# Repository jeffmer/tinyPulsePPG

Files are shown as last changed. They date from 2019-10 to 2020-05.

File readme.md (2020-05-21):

# tinyPulsePPG

This project implemented on an ATTiny85 displays a moving Photoplethysmogram together with pulse rate and estimates of SpO2 - blood oxygen percentage. It uses an SSD1306 128x32 OLED display and a Max30102 sensor. It is emphasised that this should **not be used for medical purposes**. The computation of SpO2 is very approximate and not calibrated in any way. The project is an exercise in software and hardware parsimony.

### Hardware
The system was implemented on a prototyping board as shown below:

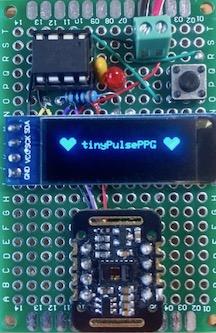
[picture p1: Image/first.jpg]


The circuit diagram is:

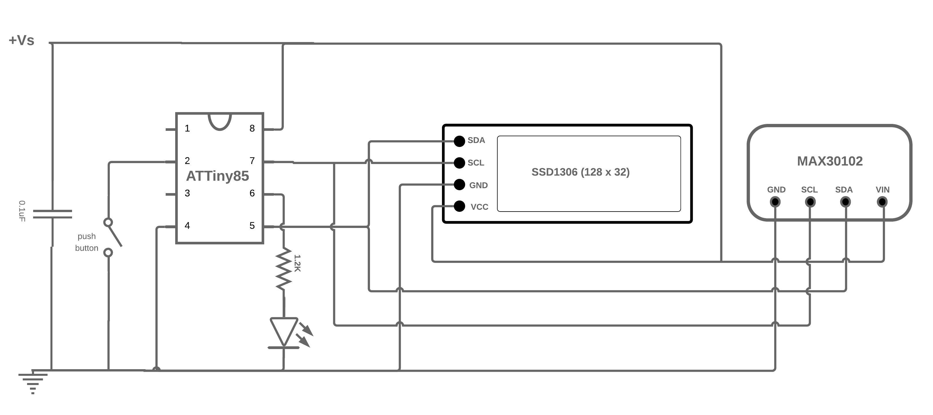
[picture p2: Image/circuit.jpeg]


The ATTiny85 is configured to run at 16 MHz using Spence Konde's ATTinyCore. Consequently, according to the datasheet, the supply voltage should be >4.5V. In fact, it seems to run quite happily from a lipo battery (3.7 - 4.2V).

### Operation

After a few seconds the following screen is displayed:

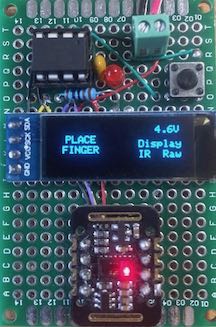
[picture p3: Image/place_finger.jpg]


When a finger is placed on the sensor, the PPG, heart-rate and two estimates of blood oxygen are displayed (discussed below):

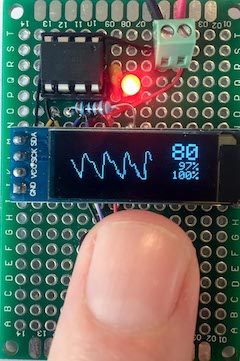
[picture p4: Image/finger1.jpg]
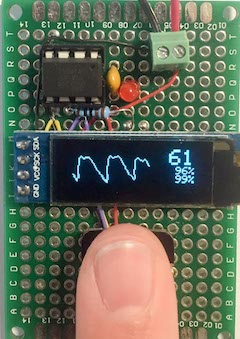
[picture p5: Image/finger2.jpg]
 ..........  

The red led pulses once per heart beat. The PPG display is updated every 50ms.

### Software

**Needed library**
In order to build this to the ATTiny85 you need to install the library ATTinyCore
This core can be installed using the boards manager. The boards manager URL is:

http://drazzy.com/package_drazzy.com_index.json

File->Preferences on a PC, or Arduino->Preferences on a Mac, enter the above URL in "Additional Boards Manager URLs
Tools -> Boards -> Boards Manager... *If using 1.6.6, close boards manager and re-open it (see below)
Select "ATTinyCore by Spence Konde" and click "Install".

**Driver issue -** The Maxim max30102 sensor used is mounted on a MH-ET LIVE breakout board. The Maxim datasheet for the max30102 implies but does not state explicitly that LED1 is Red and LED2 is Infrared (IR), however, if the amplitude of LED1 is set to zero, the red led (as depicted in the *place finger*) picture remains lit, while if LED2 is set to zero, the red led is extinguished. The obvious conclusion is that LED1 is IR and LED2 is Red (i.e. swapped) which also works when computing blood oxygen - see below. I mention this as the most common driver used in Arduino projects for the max30102 is the Sparkfun 3010x driver which clearly identifies LED1 with Red and LED2 with IR. This may be true for the max30105 device mounted on the Sparkfun board but does not seem to apply to the max30102 on the MH-ET-LIVE board. 

**Spo2 calculation** *"SpO2 stands for peripheral capillary oxygen saturation, an estimate of the amount of oxygen in the blood. More specifically, it is the percentage of oxygenated haemoglobin (haemoglobin containing oxygen) compared to the total amount of haemoglobin in the blood (oxygenated and non-oxygenated haemoglobin)."* 

Oxygenated haemoglobin and deoxygenated haemoglobin have different light absorption characteristics for red and IR wavelengths. This is the basis for sensors like the max30102. The calculation uses the ratio:

`R = (AC_red/DC_red)/(AC_IR/DC_IR)`

where `AC_xxx `is the fluctuating component of the xxx signal and `DC_xxx` is the fixed component. **tinyPulsePPG** uses R in two different formulas. The upper percentage is from the classic formula:

`R = 104 - 1.7 * R`

The lower uses a table from the Maxim Arduino driver which is an approximation of the formula:

`-45.060 * R * R + 30.354 * R + 94.845`

The AC is computed in **tinyPulsePPG** as the peak to peak amplitude of the signal after the DC element has been removed.  the DC element is computed by an exponential moving average filter and the AC is also filtered. I have not experimented enough with the constants in these filters to determine the effect on the SpO2 calculation or indeed how reliable this method is of computing these quantities.

**PPG display** The read and IR signals from the sensor go through two stages of filtering. The first as described above is removal of the DC element. The second is a moving average filter which acts as a low pass filter to remove transients before the signal is input to the beat detector. I have chosen to display the signal after the first filtering phase so that it retains more interesting features. 

For example, dicrotic notches can be seen in the pictures above - *"a secondary upstroke in the descending part of a pulse tracing corresponding to the transient increase in aortic pressure upon closure of the aortic valve. - Merriam Webster Dictionary"*

I have noticed that if this dicrotic notch is particularly strong - younger individuals - it can overcome the second stage filtering and cause erroneous output from the beat detector which essentially looks for peaks and valleys in the wave. On going work!

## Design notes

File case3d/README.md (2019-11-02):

# tinyPulsePPG - 3d printed case

The directory contains the STL files for the top and bottom of the case and the OpenScad used to generate them. 
You will need to adjust the Height of the case and the BoardHeight to fit your board and battery. The board pictured below is lower profile than the original versio (8mm).

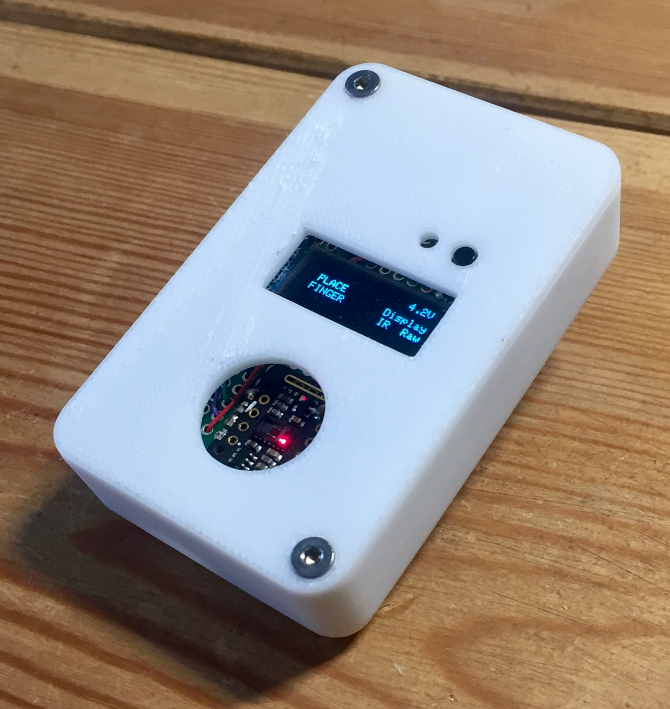
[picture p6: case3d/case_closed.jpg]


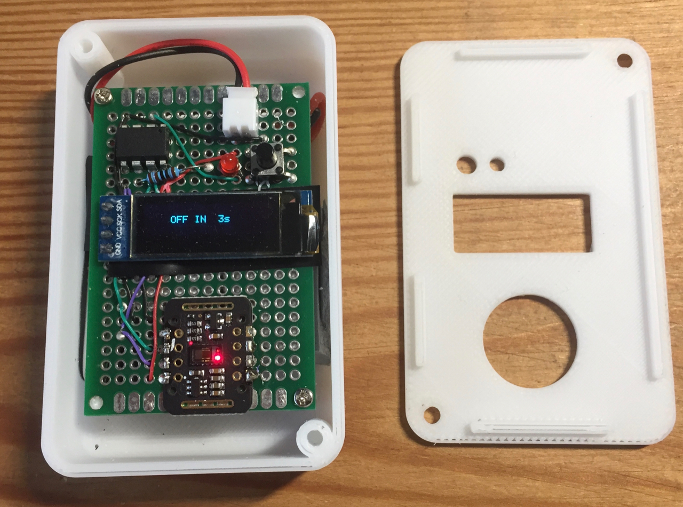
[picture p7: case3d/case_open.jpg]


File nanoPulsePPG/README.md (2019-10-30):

# arduinoPulsePPG

A version of tinyPulsePPG that runs on an Arduino AVR platform - tested on a Nano.

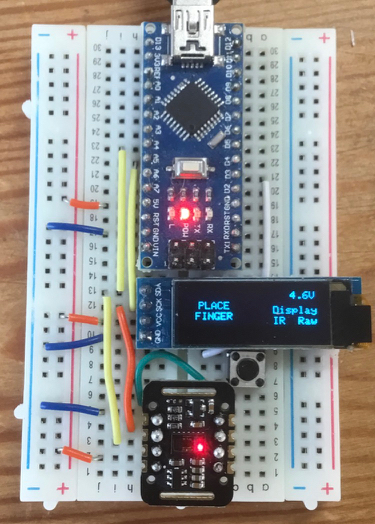
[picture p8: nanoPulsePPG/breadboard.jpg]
breadboard


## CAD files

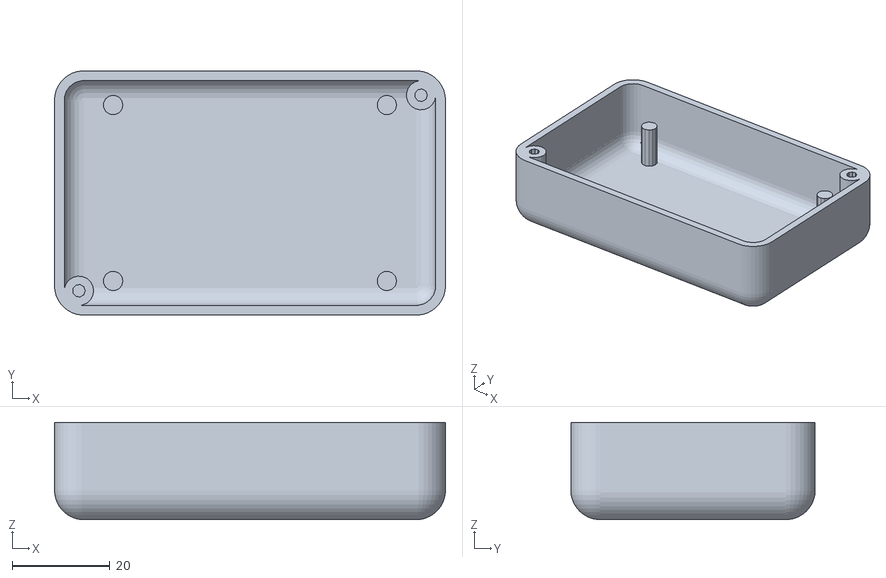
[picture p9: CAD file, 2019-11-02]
case3d/tinyPulsePPG_bottom.stl
80.0 x 50.0 x 19.9

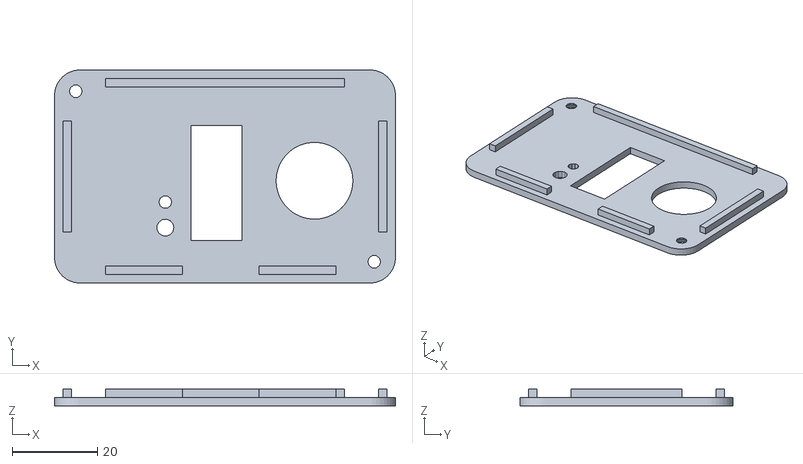
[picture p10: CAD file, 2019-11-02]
case3d/tinyPulsePPG-top.stl
80.0 x 50.0 x 3.90

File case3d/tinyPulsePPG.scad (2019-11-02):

$fa = 1.0;
$fs = 1.0;
Length = 80;
Width  = 50;
Height = 20;
Thick = 2;
Rnd    = 6;
BoardHeight = 8;

use <MCAD/boxes.scad>

module pillar(h,r) {
    difference() {
        union() {
            color("blue") cylinder(h=h,r=r);
            color("red")sphere(r=r);
        }
        translate([0,0,h/2]) cylinder(h=(h/2+1),r=1.3);
    }
}

module bottomBox(size,r){
    difference(){
        translate([size[0]/2, size[1]/2,(size[2]+r)/2]) 
            roundedBox([size[0],size[1],size[2]+r],r,false);
        translate([0,0,size[2]-0.1])
            cube([size[0],size[1],r+1]);
    }
}

module bottomCase(size,r,thick,bh){
    difference(){
        bottomBox(size,r);
        translate([thick,thick,thick]) 
            bottomBox([size[0]-thick*2, size[1]-thick*2, size[2]],r-thick);
    }
    translate([size[0]-r+1,size[1]-r+1,r-1])
        pillar(h=size[2]-r+0.88,r=3);
    translate([r-1,r-1,r-1])
        pillar(h=size[2]-r+0.88,r=3);
    translate([12,7,0.2])
        color("red") cylinder(h=size[2]-bh,r=2);
    translate([12,43,0.5])
        color("red") cylinder(h=size[2]-bh,r=2);
    translate([68,7,0.5])
        color("red") cylinder(h=size[2]-bh,r=2);
    translate([68,43,0.5])
        color("red") cylinder(h=size[2]-bh,r=2);
 }

bottomCase([Length,Width,Height],Rnd,Thick,BoardHeight);

module screwhole(thick) {
    color("red") {
        translate([0,0,-0.2]) cylinder(h=1.8,r1=3.0,r2=1.5);
        cylinder(h=thick*2,r=1.5);
    }
}

    
module topPlate(len,wid,r,thick){
    difference(){
        union() {
            translate([len/2,wid/2,thick/2])
                roundedBox([len,wid,thick],r,true);
        }
        translate([32,10,-thick])
            cube([12, 27, thick*3]);
       translate([26,13,-0.2])
            cylinder(h=thick*2,r=2); 
        translate([26,19,-0.2])
            cylinder(h=thick*2,r=1.5); 
        translate([61,24,-0.2])
            cylinder(h=thick*2,r=9); 
        translate([r-1,wid-r+1,0])
             screwhole(thick);
        translate([len-r+1,r-1,0])
             screwhole(thick);
    }
   translate([thick,2*r,thick-0.1])
       color("red") cube([thick,wid-4*r,thick]);
   translate([len-2*thick,2*r,thick-0.1])
       color("red") cube([thick,wid-4*r,thick]);
   translate([2*r,thick,thick-0.1])
       color("green") cube([30-2*r,thick,thick]);
   translate([2*r+36,thick,thick-0.1])
       color("green") cube([30-2*r,thick,thick]);
   translate([2*r,wid-2*thick,thick-0.1])
       color("green") cube([len-4*r,thick,thick]);


}

//topPlate(Length,Width,Rnd,Thick);

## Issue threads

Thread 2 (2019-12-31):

### ISSUE TITLE
Adding BME280 sensor Data

### ISSUE THREAD

**Issue by OhioJoe** [jeffmer/tinyPulsePPG#2]
I am using a 128x64 ssd1306. I can write data to oled display's lower half. I would like to have the PulseOxy data display on the first 31 lines and the BME sensor data display on lines 33-63. 
I can add 'test' data ie: temp = 98.6 but cannot figure out how to add live data.
I added a function to calculate the variables, but calling the function hangs the program.  

> void draw_oled(int msg) {
>   oled.firstPage();
> 
>   do {
>     switch (msg) {
>       case 0:  oled.drawStr(10, 0, F("Device error"), 1);
>         break;
>       case 1:
>         oled.drawStr(13, 2, F("PLACE"), 1); //13,10
>         oled.drawStr(10, 16, F("FINGER"), 1); //10,20
>         oled.drawChar(100, 0, voltage / 10 + '0');
>         oled.drawChar(106, 0, '.');
>         oled.drawChar(112, 0, voltage % 10 + '0');
>         oled.drawChar(118, 0, 'V');
>         oled.drawStr(84, 16, F("Display"), 1); //84,14
>         oled.drawStr(0, 34, F("T: "), 1);
>         oled.drawChar(26, 34,  'F');
> //        temp = 1.8 * bme280.readTemperature() + 32;
>         temp = 98.6;
>         //        Serial.println(temp);
>         print_digit(12, 34, temp, "F", 2, 1);
>         oled.drawStr(64, 34, F("H: "), 1);
>         print_digit(76, 34, humi, "F", 2, 1);
>         oled.drawChar(94, 34,  '%');
>         oled.drawStr(0, 45, F("Alt: "), 1);
> 
>         print_digit(25, 45, alt, "F", 3, 1);
>         oled.drawStr(0, 57, F("P: "), 1);
>         print_digit(12, 57, pres, "F", 3, 1);
>         oled.drawStr(34, 57, F("mmHg"), 1);
>         if (draw_Red)
>           oled.drawStr(84, 24, F("Red"), 1);
>         else
>           oled.drawStr(84, 24, F("IR"), 1);
>         if (filter_for_graph)
>           oled.drawStr(108, 24, F("Avg"), 1);
>         else
>           oled.drawStr(108, 24, F("Raw"), 1);
>         break;

**Comment by jeffmer** [comment]
I would suggest you make temp a global variable and call your function in the main program loop. The problem is that to avoid having a large buffer the draw routines are called multiple times. I suspect you are hanging due to an i2c conflict.

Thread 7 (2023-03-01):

### ISSUE TITLE
Image example usage

### ISSUE THREAD

**Issue by Arritmic** [jeffmer/tinyPulsePPG#7]
Hi @jeffmer ,

Could I use one of the images of the device prototype in my thesis?
If yes, how should I reference you??

Best,
Arritmic

**Comment by jeffmer** [comment]
Yes of course, feel free to use it. Simply reference the github repository would be fine. 

BTW: what is your thesis about?

**Comment by Arritmic** [comment]
It is about remote photoplethysmography and remote ballistography using cameras and radars. It includes from development of novel algorithms, to use cases and implementation in embedded devices.

**Comment by jeffmer** [comment]
That sounds like a lot of fun. I am a retired computing science academic - would love to see your thesis when you finish it - I am sure you will put a PDF on line.

**Comment by Arritmic** [comment]
Yes, sure!! It will be an honor. Please, find my humble contribution in google scholar: https://scholar.google.fi/citations?user=vLYIwqUAAAAJ&hl=en

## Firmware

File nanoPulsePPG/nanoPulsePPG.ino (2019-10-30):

/*
*  ATTiny84 - Pulse Oximeter with PPG display
*  DEFINITELY NOT FOR MEDICAL USE
*
* j.n.magee 15-10-2019
*/

#include "ssd1306h.h"
#include "MAX30102.h"
#include "Pulse.h"
#include <avr/pgmspace.h>
#include <EEPROM.h>
#include <avr/sleep.h>

// Routines to clear and set bits 
#ifndef cbi
#define cbi(sfr, bit) (_SFR_BYTE(sfr) &= ~_BV(bit))
#endif
#ifndef sbi
#define sbi(sfr, bit) (_SFR_BYTE(sfr) |= _BV(bit))
#endif


SSD1306 oled; 
MAX30102 sensor;
Pulse pulseIR;
Pulse pulseRed;
MAFilter bpm;

#define LED LED_BUILTIN
#define BUTTON 3
#define OPTIONS 7

static const uint8_t heart_bits[] PROGMEM = { 0x00, 0x00, 0x38, 0x38, 0x7c, 0x7c, 0xfe, 0xfe, 0xfe, 0xff, 
                                        0xfe, 0xff, 0xfc, 0x7f, 0xf8, 0x3f, 0xf0, 0x1f, 0xe0, 0x0f,
                                        0xc0, 0x07, 0x80, 0x03, 0x00, 0x01, 0x00, 0x00, 0x00, 0x00, 
                                        0x00, 0x00 };

//spo2_table is approximated as  -45.060*ratioAverage* ratioAverage + 30.354 *ratioAverage + 94.845 ;
const uint8_t spo2_table[184] PROGMEM =
        { 95, 95, 95, 96, 96, 96, 97, 97, 97, 97, 97, 98, 98, 98, 98, 98, 99, 99, 99, 99, 
          99, 99, 99, 99, 100, 100, 100, 100, 100, 100, 100, 100, 100, 100, 100, 100, 100, 100, 100, 100, 
          100, 100, 100, 100, 99, 99, 99, 99, 99, 99, 99, 99, 98, 98, 98, 98, 98, 98, 97, 97, 
          97, 97, 96, 96, 96, 96, 95, 95, 95, 94, 94, 94, 93, 93, 93, 92, 92, 92, 91, 91, 
          90, 90, 89, 89, 89, 88, 88, 87, 87, 86, 86, 85, 85, 84, 84, 83, 82, 82, 81, 81, 
          80, 80, 79, 78, 78, 77, 76, 76, 75, 74, 74, 73, 72, 72, 71, 70, 69, 69, 68, 67, 
          66, 66, 65, 64, 63, 62, 62, 61, 60, 59, 58, 57, 56, 56, 55, 54, 53, 52, 51, 50, 
          49, 48, 47, 46, 45, 44, 43, 42, 41, 40, 39, 38, 37, 36, 35, 34, 33, 31, 30, 29, 
          28, 27, 26, 25, 23, 22, 21, 20, 19, 17, 16, 15, 14, 12, 11, 10, 9, 7, 6, 5, 
          3, 2, 1 } ;


int getVCC() {
  //reads internal 1V1 reference against VCC
  #if defined(__AVR_ATmega1284P__)
    ADMUX = _BV(REFS0) | _BV(MUX4) | _BV(MUX3) | _BV(MUX2) | _BV(MUX1);  // For ATmega1284
  #else
    ADMUX = _BV(REFS0) | _BV(MUX3) | _BV(MUX2) | _BV(MUX1);  // For ATmega328
  #endif
  delay(2); // Wait for Vref to settle
  ADCSRA |= _BV(ADSC); // Convert
  while (bit_is_set(ADCSRA, ADSC));
  uint8_t low = ADCL;
  unsigned int val = (ADCH << 8) | low;
  //discard previous result
  ADCSRA |= _BV(ADSC); // Convert
  while (bit_is_set(ADCSRA, ADSC));
  low = ADCL;
  val = (ADCH << 8) | low;
  
  return (((long)1024 * 1100) / val)/100;  
}

void print_digit(int x, int y, long val, char c=' ', uint8_t field = 3,
                    const int BIG = 2){  
    uint8_t ff = field;
    do { 
        char ch = (val!=0) ? val%10+'0': c;
        oled.drawChar( x+BIG*(ff-1)*6, y, ch, BIG);
        val = val/10; 
        --ff;
    } while (ff>0);
}


/*
 *   Record, scale  and display PPG Wavefoem
 */
const uint8_t MAXWAVE = 72;

class Waveform {
  public:
    Waveform(void) {wavep = 0;}

      void record(int waveval) {
        waveval = waveval/8;         // scale to fit in byte
        waveval += 128;              //shift so entired waveform is +ve
        waveval = waveval<0? 0 : waveval;
        waveform[wavep] = (uint8_t) (waveval>255)?255:waveval; 
        wavep = (wavep+1) % MAXWAVE;
      }
  
      void scale() {
        uint8_t maxw = 0;
        uint8_t minw = 255;
        for (int i=0; i<MAXWAVE; i++) { 
          maxw = waveform[i]>maxw?waveform[i]:maxw;
          minw = waveform[i]<minw?waveform[i]:minw;
        }
        uint8_t scale8 = (maxw-minw)/4 + 1;  //scale * 8 to preserve precision
        uint8_t index = wavep;
        for (int i=0; i<MAXWAVE; i++) {
          disp_wave[i] = 31-((uint16_t)(waveform[index]-minw)*8)/scale8;
          index = (index + 1) % MAXWAVE;
        }
      }

      void draw(uint8_t X) {
       for (int i=0; i<MAXWAVE; i++) {
        uint8_t y = disp_wave[i];
        oled.drawPixel(X+i, y);
        if (i<MAXWAVE-1) {
          uint8_t nexty = disp_wave[i+1];
          if (nexty>y) {
            for (uint8_t iy = y+1; iy<nexty; ++iy)  oled.drawPixel(X+i, iy);
          } else if (nexty<y) {
            for (uint8_t iy = nexty+1; iy<y; ++iy)  oled.drawPixel(X+i, iy);
          }
        }
      }  
    }

private:
    uint8_t waveform[MAXWAVE];
    uint8_t disp_wave[MAXWAVE];
    uint8_t wavep = 0;
    
} wave;

int  beatAvg;
int  SPO2, SPO2f;
int  voltage;
bool filter_for_graph = false;
bool draw_Red = false;
uint8_t pcflag =0;
uint8_t istate = 0;
uint8_t sleep_counter = 0;
void button(void){
    pcflag = 1;
}

void checkbutton(){
    if (pcflag && !digitalRead(BUTTON)) {
      istate = (istate +1) % 4;
      filter_for_graph = istate & 0x01;
      draw_Red = istate & 0x02;
      EEPROM.write(OPTIONS, filter_for_graph);
      EEPROM.write(OPTIONS+1, draw_Red);
    }
    pcflag = 0;
}

void go_sleep() {
    oled.fill(0);
    oled.off();
    delay(10);
    sensor.off();
    delay(10);
    cbi(ADCSRA, ADEN);  // disable adc
    delay(10);
    pinMode(0,INPUT);
    pinMode(2,INPUT);
    set_sleep_mode(SLEEP_MODE_PWR_DOWN);     
    sleep_mode();  // sleep until button press 
    // cause reset
    setup();
}

void draw_oled(int msg) {
    oled.firstPage();
    do{
    switch(msg){
        case 0:  oled.drawStr(10,0,F("Device error"),1); 
                 break;
        case 1:  oled.drawStr(13,10,F("PLACE"),1); 
                 oled.drawStr(10,20,F("FINGER"),1);
                 oled.drawChar(100,0,voltage/10+'0');
                 oled.drawChar(106,0,'.');
                 oled.drawChar(112,0,voltage%10+'0');
                 oled.drawChar(118,0,'V');
                 oled.drawStr(84,14,F("Display"),1); 
                 if (draw_Red) 
                    oled.drawStr(84,24,F("Red"),1); 
                 else
                    oled.drawStr(84,24,F("IR"),1); 
                 if (filter_for_graph) 
                    oled.drawStr(108,24,F("Avg"),1); 
                 else
                    oled.drawStr(108,24,F("Raw"),1); 
                 break;
        case 2:  print_digit(86,0,beatAvg);
                 wave.draw(8);
                 print_digit(98,16,SPO2f,' ',3,1);
                 oled.drawChar(116,16,'%');
                 print_digit(98,24,SPO2,' ',3,1);
                 oled.drawChar(116,24,'%');
                 break;
        case 3:  oled.drawStr(28,12,F("tinyPulsePPG"),1);
                 oled.drawXBMP(6,8,16,16,heart_bits);
                 oled.drawXBMP(106,8,16,16,heart_bits);
                 break;
        case 4:  oled.drawStr(28,12,F("OFF IN"),1);
                 oled.drawChar(76,12,10-sleep_counter/10+'0');
                 oled.drawChar(82,12,'s');
                 break;
        }
    } while (oled.nextPage());
}

void setup(void) {
  pinMode(LED, OUTPUT);
  pinMode(BUTTON, INPUT_PULLUP);
  filter_for_graph = EEPROM.read(OPTIONS);
  draw_Red = EEPROM.read(OPTIONS+1);
  oled.init();
  oled.fill(0x00);
  draw_oled(3);
  delay(3000); 
  if (!sensor.begin())  {
    draw_oled(0);
    while (1);
  }
  sensor.setup(); 
  attachInterrupt(digitalPinToInterrupt(BUTTON),button, CHANGE);
}

long lastBeat = 0;    //Time of the last beat 
long displaytime = 0; //Time of the last display update
bool led_on = false;


void loop()  {
    sensor.check();
    long now = millis();   //start time of this cycle
    if (!sensor.available()) return;
    uint32_t irValue = sensor.getIR(); 
    uint32_t redValue = sensor.getRed();
    sensor.nextSample();
    if (irValue<5000) {
        voltage = getVCC();
        checkbutton();
        draw_oled(sleep_counter<=70 ? 1 : 4); // finger not down message
        delay(100);
        ++sleep_counter;
        if (sleep_counter>100) {
          go_sleep(); 
          sleep_counter = 0;
        }
    } else {
        sleep_counter = 0;
        // remove DC element
        int16_t IR_signal, Red_signal;
        bool beatRed, beatIR;
        if (!filter_for_graph) {
           IR_signal =  pulseIR.dc_filter(irValue) ;
           Red_signal = pulseRed.dc_filter(redValue);
           beatRed = pulseRed.isBeat(pulseRed.ma_filter(Red_signal));
           beatIR =  pulseIR.isBeat(pulseIR.ma_filter(IR_signal));        
        } else {
           IR_signal =  pulseIR.ma_filter(pulseIR.dc_filter(irValue)) ;
           Red_signal = pulseRed.ma_filter(pulseRed.dc_filter(redValue));
           beatRed = pulseRed.isBeat(Red_signal);
           beatIR =  pulseIR.isBeat(IR_signal);
        }
        // invert waveform to get classical BP waveshape
        wave.record(draw_Red ? -Red_signal : -IR_signal ); 
        // check IR or Red for heartbeat     
        if (draw_Red ? beatRed : beatIR){
            long btpm = 60000/(now - lastBeat);
            if (btpm > 0 && btpm < 200) beatAvg = bpm.filter((int16_t)btpm);
            lastBeat = now; 
            digitalWrite(LED, HIGH); 
            led_on = true;
            // compute SpO2 ratio
            long numerator   = (pulseRed.avgAC() * pulseIR.avgDC())/256;
            long denominator = (pulseRed.avgDC() * pulseIR.avgAC())/256;
            int RX100 = (denominator>0) ? (numerator * 100)/denominator : 999;
            // using formula
            SPO2f = (10400 - RX100*17+50)/100;  
            // from table
            if ((RX100>=0) && (RX100<184))
              SPO2 = pgm_read_byte_near(&spo2_table[RX100]);
        }
        // update display every 50 ms if fingerdown
        if (now-displaytime>50) {
            displaytime = now;
            wave.scale();
            draw_oled(2);
        }
    }
    // flash led for 25 ms
    if (led_on && (now - lastBeat)>25){
        digitalWrite(LED, LOW);
        led_on = false;
     }
}

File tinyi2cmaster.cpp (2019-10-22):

/* Tiny I2C

   David Johnson-Davies - www.technoblogy.com - 14th April 2018
   
   CC BY 4.0
   Licensed under a Creative Commons Attribution 4.0 International license: 
   http://creativecommons.org/licenses/by/4.0/
*/

#include "TinyI2CMaster.h"

TinyI2CMaster::TinyI2CMaster() 
{
}

// Minimal Tiny I2C Routines **********************************************

uint8_t TinyI2CMaster::transfer (uint8_t data) {
  USISR = data;                               // Set USISR according to data.
                                              // Prepare clocking.
  data = 0<<USISIE | 0<<USIOIE |              // Interrupts disabled
         1<<USIWM1 | 0<<USIWM0 |              // Set USI in Two-wire mode.
         1<<USICS1 | 0<<USICS0 | 1<<USICLK |  // Software clock strobe as source.
         1<<USITC;                            // Toggle Clock Port.
  do {
    DELAY_T2TWI;
    USICR = data;                             // Generate positive SCL edge.
    while (!(PIN_USI_CL & 1<<PIN_USI_SCL));   // Wait for SCL to go high.
    DELAY_T4TWI;
    USICR = data;                             // Generate negative SCL edge.
  } while (!(USISR & 1<<USIOIF));             // Check for transfer complete.

  DELAY_T2TWI;
  data = USIDR;                               // Read out data.
  USIDR = 0xFF;                               // Release SDA.
  DDR_USI |= (1<<PIN_USI_SDA);                // Enable SDA as output.

  return data;                                // Return the data from the USIDR
}

void TinyI2CMaster::init () {
  PORT_USI |= 1<<PIN_USI_SDA;                 // Enable pullup on SDA.
  PORT_USI_CL |= 1<<PIN_USI_SCL;              // Enable pullup on SCL.

  DDR_USI_CL |= 1<<PIN_USI_SCL;               // Enable SCL as output.
  DDR_USI |= 1<<PIN_USI_SDA;                  // Enable SDA as output.

  USIDR = 0xFF;                               // Preload data register with "released level" data.
  USICR = 0<<USISIE | 0<<USIOIE |             // Disable Interrupts.
          1<<USIWM1 | 0<<USIWM0 |             // Set USI in Two-wire mode.
          1<<USICS1 | 0<<USICS0 | 1<<USICLK | // Software stobe as counter clock source
          0<<USITC;
  USISR = 1<<USISIF | 1<<USIOIF | 1<<USIPF | 1<<USIDC | // Clear flags,
          0x0<<USICNT0;                       // and reset counter.
}


uint8_t TinyI2CMaster::read (void) {
  if ((I2Ccount != 0) && (I2Ccount != -1)) I2Ccount--;
  
  /* Read a byte */
  DDR_USI &= ~1<<PIN_USI_SDA;                 // Enable SDA as input.
  uint8_t data = TinyI2CMaster::transfer(USISR_8bit);

 /* Prepare to generate ACK (or NACK in case of End Of Transmission) */
  if (I2Ccount == 0) USIDR = 0xFF; else USIDR = 0x00;
  TinyI2CMaster::transfer(USISR_1bit);                 // Generate ACK/NACK.

  return data;                                // Read successfully completed
}

uint8_t TinyI2CMaster::readLast (void) {
  I2Ccount = 0;
  return TinyI2CMaster::read();
}

bool TinyI2CMaster::write (uint8_t data) {
  /* Write a byte */
  PORT_USI_CL &= ~(1<<PIN_USI_SCL);           // Pull SCL LOW.
  USIDR = data;                               // Setup data.
  TinyI2CMaster::transfer(USISR_8bit);                 // Send 8 bits on bus.

  /* Clock and verify (N)ACK from slave */
  DDR_USI &= ~(1<<PIN_USI_SDA);               // Enable SDA as input.
  if (TinyI2CMaster::transfer(USISR_1bit) & 1<<TWI_NACK_BIT) return false;

  return true;                                // Write successfully completed
}

// Start transmission by sending address
bool TinyI2CMaster::start (uint8_t address, int readcount) {
  if (readcount != 0) { I2Ccount = readcount; readcount = 1; }
  uint8_t addressRW = address<<1 | readcount;

  /* Release SCL to ensure that (repeated) Start can be performed */
  PORT_USI_CL |= 1<<PIN_USI_SCL;              // Release SCL.
  while (!(PIN_USI_CL & 1<<PIN_USI_SCL));     // Verify that SCL becomes high.
#ifdef TWI_FAST_MODE
  DELAY_T4TWI;
#else
  DELAY_T2TWI;
#endif

  /* Generate Start Condition */
  PORT_USI &= ~(1<<PIN_USI_SDA);              // Force SDA LOW.
  DELAY_T4TWI;
  PORT_USI_CL &= ~(1<<PIN_USI_SCL);           // Pull SCL LOW.
  PORT_USI |= 1<<PIN_USI_SDA;                 // Release SDA.

  if (!(USISR & 1<<USISIF)) return false;

  /*Write address */
  PORT_USI_CL &= ~(1<<PIN_USI_SCL);           // Pull SCL LOW.
  USIDR = addressRW;                          // Setup data.
  TinyI2CMaster::transfer(USISR_8bit);                 // Send 8 bits on bus.

  /* Clock and verify (N)ACK from slave */
  DDR_USI &= ~(1<<PIN_USI_SDA);               // Enable SDA as input.
  if (TinyI2CMaster::transfer(USISR_1bit) & 1<<TWI_NACK_BIT) return false; // No ACK

  return true;                                // Start successfully completed
}

bool TinyI2CMaster::restart(uint8_t address, int readcount) {
  return TinyI2CMaster::start(address, readcount);
}

void TinyI2CMaster::stop (void) {
  PORT_USI &= ~(1<<PIN_USI_SDA);              // Pull SDA low.
  PORT_USI_CL |= 1<<PIN_USI_SCL;              // Release SCL.
  while (!(PIN_USI_CL & 1<<PIN_USI_SCL));     // Wait for SCL to go high.
  DELAY_T4TWI;
  PORT_USI |= 1<<PIN_USI_SDA;                 // Release SDA.
  DELAY_T2TWI;
}

TinyI2CMaster TinyI2C = TinyI2CMaster();      // Instantiate a TinyI2C object
